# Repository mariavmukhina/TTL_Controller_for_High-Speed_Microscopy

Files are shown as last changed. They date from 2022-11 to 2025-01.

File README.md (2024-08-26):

# TTL Controller for High-Speed Microscopy 

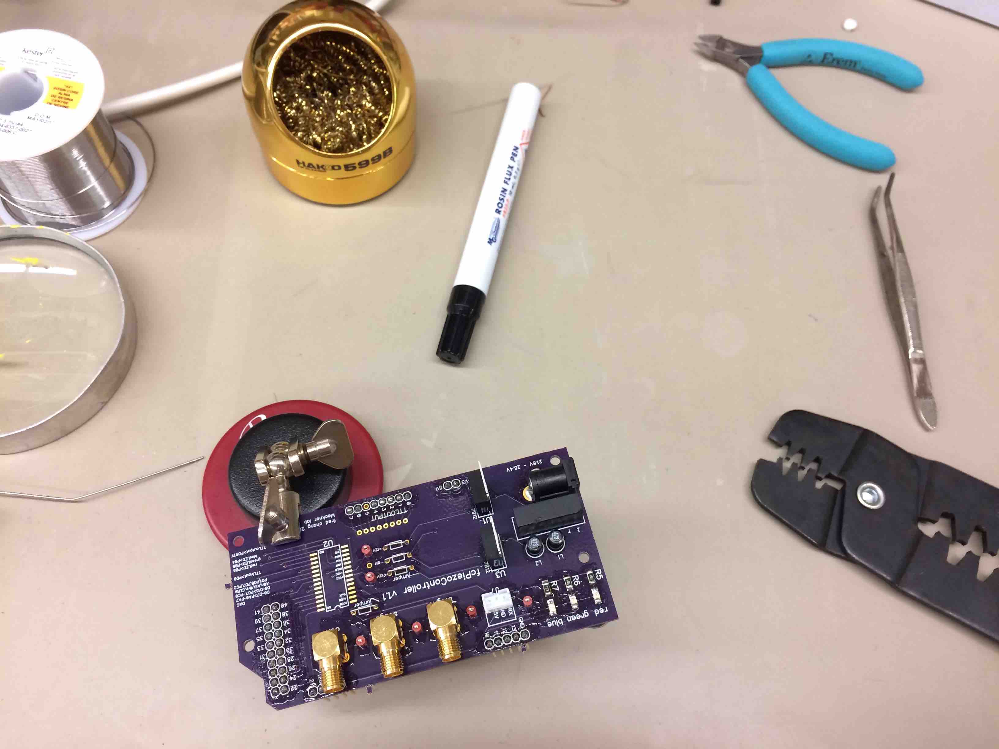
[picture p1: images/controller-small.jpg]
  

An inexpensive Transistor-Transistor Logic (TTL) controller consisting of Arduino and custom-made printed board that listens to firing TTL pulse from camera and generates up to 8 TTL output pulses. [Software for the controller](https://github.com/mariavmukhina/ScopeScript/tree/main/hardwareControl/piezoController/arduinoFirmware) in Arduino programming language allows to synchronize camera image acquisition with turning on epi or brightfield illumination, moving the piezoelectric Z stage, and applying mechanical deformations to the sample with nanomanipulator, as shown below. 

The unique feature of the controller is fast aqcuisition in 3D, which is achieved by sending the full "recipe" for a 3D stack to the piezoelectric Z stage before the acquisition starts. In the test experiments, the controller coupled to PI NanoZ stage and sCMOS Hamamatsu Flash 4.0 V3 camera enabled acquisition over a volume up to 133x133x100 µm^3 in 1.42 sec that is equivalent to the rate of 2.9x10^8 voxels/sec (with 10 msec exposure per z slice and 1 µm axial resolution). 

The provided files contain design files for the custom printed circuit board (PCB, can be ordered from https://oshpark.com/), the parts list for the PCB, and soldering and assembling instructions.

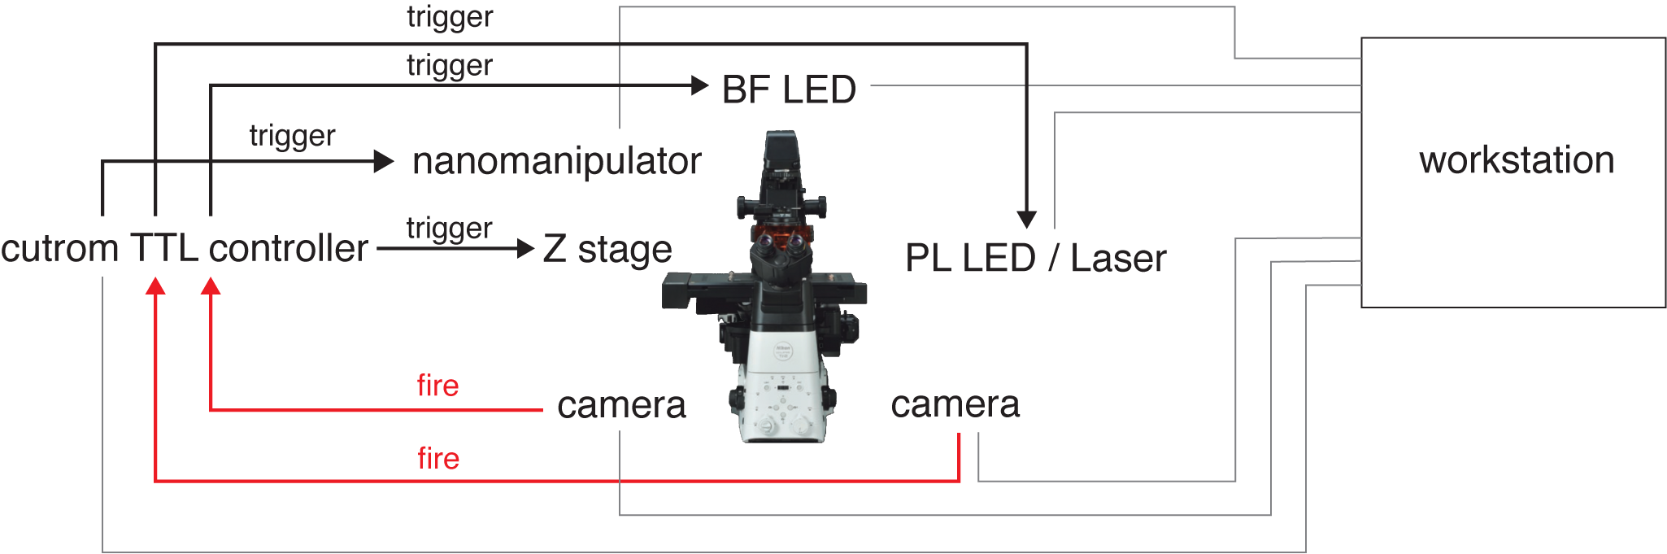
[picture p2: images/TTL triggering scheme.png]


Have a question? Get in touch! You can raise a support [issue](https://github.com/mariavmukhina/TTL_Controller_for_Microscope/issues/new?assignees=mariavmukhina&labels=help+wanted&template=support-request.md&title=%5BSUPPORT%5D).

Frederick Chang designed and programmed the controller (2017). Maria Mukhina introduced changes to the board design to add additional epi channel and new TTL output for optional peripheral device (2020). 

## Kleckner Lab Acknowledgement

Please acknowledge the Kleckner Lab in your publications. An appropriate wording would be: "The TTL controller design was provided by the laboratory of Nancy Kleckner at Harvard University, funded in part by National Institutes of Health (NIH) grant R35GM136322."

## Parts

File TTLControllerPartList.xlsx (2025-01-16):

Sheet: Sheet1
 |  | Frederick Chang, Maria Mukhina - Kleckner Lab
Board Name | Function | Part Name |  | FootPrint | Quantity | Sub
Digikey Part No.
 |  | ARDUINO MEGA ADK BOARD REV3 | 1050-1018-ND | NA | 1
TOP of the board
J1 | power supply 24V - 1A, anything outside the indicated range will break the board | CONN PWR JACK 2.1X5.5MM SOLDER | EJ508A-ND | 2.10mm ID (0.083"), 5.50mm OD (0.217") | 1
 |  | AC/DC WALL MOUNT ADAPTER 24V 24W | 102-3628-ND | Barrel Plug R/A, 2.1mm I.D. x 5.5mm O.D. x 9.5mm | 1
U4 | DC/DC converter, takes 24V input and gives out -15 to +15 V | DC/DC CONVERTER +/-15V 1W | 811-2174-5-ND |  | 1
L1-L2 |  | FIXED IND 47UH 500MA 540 MOHM TH | 811-2028-ND |  | 2
R5-R7 | reporter LEDs, see Arduino code for meanings | RES SMD 10K OHM 5% 1/4W 1206 | 311-10KERTR-ND | 1206 (3216 Metric) | 3
blue |  | LED BLUE CLEAR 1206 SMD | 160-1643-2-ND | 1206 (3216 Metric) | 1
green |  | LED GREEN CLEAR 1206 SMD | 160-1456-2-ND | 1206 (3216 Metric) | 1
red |  | LED RED CLEAR 1206 SMD | 160-1457-2-ND | 1206 (3216 Metric) | 1
T |  | TEST POINT PC MINI .040"D RED | 36-5000-ND | 0.040" (1.02mm) Hole Diameter | 6
U1 | linear regulator cleans up noisy -15 : +15 V signal to give -12 : +12 V | IC REG LDO -12V 1A TO220-3 | MC7912CTGOS-ND | TO-220 | 1
U3 |  | IC REG LINEAR 12V 1A TO220AB | MC7812BTGOS-ND | TO-220 | 1
J7 | LCD screen connection | CONN HEADER VERT 3POS 2MM | 455-B3B-PH-KL-ND | 0.079" (2.00mm) pitch | 1
 | Stand for LCD sceen | HEX STANDOFF 4-40 ALUMINUM 1" | 36-1897-ND |  | 4
 | screws for LCD screen | MACHINE SCREW PAN PHILLIPS 4-40 | 335-1082-ND |  | 8
 | connection to LCD screen | JUMPER SPH-002T-P0.5S X2 2" | 455-3081-ND | 2'' jumpered cable | 3
 |  | CONN HOUSING PH 3POS 2.0MM | 455-1126-ND | 0.079" (2.00mm) | 2
cam,stage,bright | SMA connector jacks for camera input and brightfield LED and stage outputs | CONN SMA JACK R/A 50 OHM PCB FEMALE | SAM8856-ND |  | 3
 | SMA-to-BNC connectors for the camera, brightfield LED and stage | SMA male to BNC male 24'' | ACX1719-ND |  | 3
 | cable connection for brightfield LED (Scope LED) | CONN ADAPT JACK-JACK BNC 50 OHM | ARF1069-ND |  | 1
 |  | CONN D-SUB PLUG 15POS W/O CONT | A31504-ND |  | 1
 |  | CONN D-SUB PIN PCB GOLD | A122223-ND |  | 1
 |  | 7.0" (177.80mm) BNC Male Plug To Wire Lead Test Lead | 314-1189-ND |  | 1
J8 | connector header with 5 channels for Epi Light source | CONN HEADER VERT 5POS 2MM | 455-1707-ND | 0.079" (2.00mm) | 1
 | cable connection to Epi light source (CoolLED) | CABLE JST PHR-05 AWG 24 200MM | 1460-1296-ND | 0.079" (2.00mm) | 1
 |  | CONN D-SUB HD RCPT 15POS STR | AE11025-ND | Dsub15 female socket | 1
 |  | CONN D-SUB HD HOUSING PLUG 15POS | 1122-1175-ND | Dsub15 housing for male pins | 1
 |  | CONN D-SUB PIN PCB GOLD | A122223-ND | D sub male contacts | 1
 |  | CONN HOOD D-SUB 15POS PLASTIC | AE11015-ND | DB15 housing 15 pos | 2
 |  | Cable Assembly Coaxial BNC to Cable RG-58C 60.0" (1.5m) 5.0' | 501-1693-ND |  | 5
 |  | KIT SHRINK TUBING 2:1 XLPO MULTI | FKIT221CMC032-ND | tubing for contacts isolation | 1
U2 | DAC | IC 16BIT UNIPOLAR D/A 28SOIC | 296-24945-5-ND | IC 16BIT UNIPOLAR D/A 28SOIC | 1 | 2156-DAC715UK-ND
BOTTOM of the board
1uF | capacitors for power supply | CAP TANT 1UF 35V 20% 1411 | 399-10228-1-ND | 1411 | 6
0.33uF |  | CAP TANT 0.33UF 50V 20% 1411 | 399-3718-1-ND | 1411 | 1
2.2uF |  | CAP TANT 2.2UF 35V 10% 1411 | 399-8307-1-ND | 1411 | 1
 | сonnection to Arduino | CONN HEADER 50POS .100" SGL GOLD | SAM1061-50-ND |  | 1
 | сonnection to Arduino | CONN HEADER 10POS .100" DL GOLD | SAM1060-05-ND |  | 1
SparkFun no.
 | LCD screen | SparkFun Serial Enabled LCD Kit | LCD-10097 |  | 1
 |  |  | Сustom made
jumpers | jumpers connect gaps in the board connectivity; can be installed or removed; if installed, make a testing points, can be used to hook up oscilloscope; helpful in prototyping and diagnostics | ~1 cm long piece of wire bent in U-shape |  |  | 4

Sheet: soldering
CONICAL TIP (GT4), SHARP, ( X L) | 5358-GT4-CN1505A-ND
CHISEL TIP (GT4), (W X L) 1.0 MM | 5358-GT4-CH0010S-ND
Metcal 90 WATT GT SOLDERING SYSTEM | 5358-GT90-HP-T4-ND (https://www.digikey.com/en/products/detail/metcal/GT90-HP-T4/22478559)
PEN RA ROSIN FLUX .34OZ W/TIP | 473-1033-ND
ADJUSTABLE CIRCUIT BOARD HOLDER | 243-1223-ND
SLDR SCOURPAD W/HLDR MTL BRSS WL | 1691-1006-ND
SOLDER RA 60/40 18AWG 1LB | KE1105-ND
CUTTER SIDE OVAL SPR FULL FLUSH | 632N-ND
KLEIN KURVE WIRE STRIPPER & CRIM | 1742-1680-ND
MULTMTR ELEC DMM W/NON CNT VOLT | 614-1011-ND
DESOLDER BRAID ROSIN 0.05" 25' | 473-1065-ND
FA400-04 American Hakko Products, Inc. FUME ABSORBER BENCH TOP | 1691-1039-ND (https://www.digikey.com/en/products/detail/american-hakko-products-inc/FA400-04/6228795)
4140A-P MG Chemicals FLUX REMOVER PEN- CARB COMPLIANT | 473-1267-ND (https://www.digikey.com/en/products/detail/mg-chemicals/4140A-P/7930792)
Rigol Technologies / DHO814 | 2211-DHO814-ND

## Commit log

2024-06-13 Delete TTLControllerPartList.xlsx
    Updated version is uploaded
    [TTLControllerPartList.xlsx]
2024-06-13 Updated version from 06/2024
    [TTLControllerPartList.xlsx]
2024-07-18 Add files via upload
    Updated version from 07/2024
    [TTLControllerPartList.xlsx]
2025-01-16 Parts # updated
    [TTLControllerPartList.xlsx]
